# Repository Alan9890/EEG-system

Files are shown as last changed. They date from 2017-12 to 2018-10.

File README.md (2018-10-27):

# EEG-system

NB: If you choose to replicate this project, you do so at your own risk. This is a project that electrically interacts with the human body, and as such there are risks involved. I have designed this system to be as safe as I can make it, but you should still proceed with caution.

This personal project came about as a way to merge two of my interests: physiology and electronics. Electrophysiological signals are the measurable electrical signatures associated with physiological processes. Examples include ECG and EMG for heart and muscle activity respectively. 

## The current state of the project:
Features:
* **Up to 8 channels with 24-bit resolution.** The ADS1298 chip is capable of a maximum of sampling all eight channels at 32k samples/second, but the real limitation is the microcontroller. Practically, a single channel can be broadcast over wifi at about 1000 samples/second. Higher rates can be achieved over a wired connection, or if upgrading the microcontroller.
* **Input referred noise < 5 uV peak-to-peak** (demonstrated to be suitable for EEG, including
SSVEP-based brain-computer interfaces). The system includes up to 12x programmable gain.
* **Battery-powered** for portability, to reduce risk of electric shock, and mitigate contamination from AC noise.
* **Custom GUI** written in Python for device control, data capture, visualization, and analysis
* Capabilities include measuring heart (ECG), muscle (EMG) and brain (EEG) signals.

This repository documents a combination of a python GUI, NodeMCU/arduino code and a PCB design to create a system for acquisition of biological signals. At this point, this project repo includes hardware schematics, circuit board layouts (Eagle CAD files) and firmware (C++), as well as user interface GUI (Python 3.6) which can do the following:
* Connect to a WiFi network and start data collection
* Display real-time readings being collected by the hardware, as well as FFT (frequency spectrum) display.
* Record the time-domain data to a CSV file
* Reset the device
* Toggle the 50 Hz notch filter or high-pass filter on or off
* Change the signal source to choose between the electrodes, the internally generated test signal, or internally shorting the inputs
* Select a different sampling rate, input channel or amplifier gain
* Display the maximum frequency of the signal in the current display window

Below is a photo of the EEG-capturing hardware:

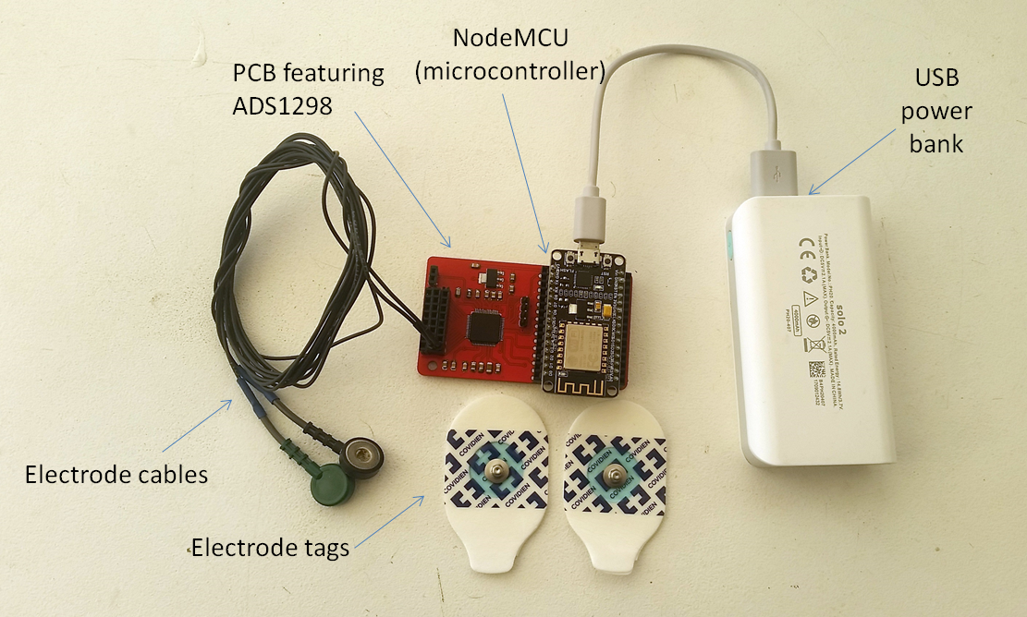
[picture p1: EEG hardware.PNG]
Hardware


Below is a demo of the system capturing alpha waves over my occipital lobe (red text added):

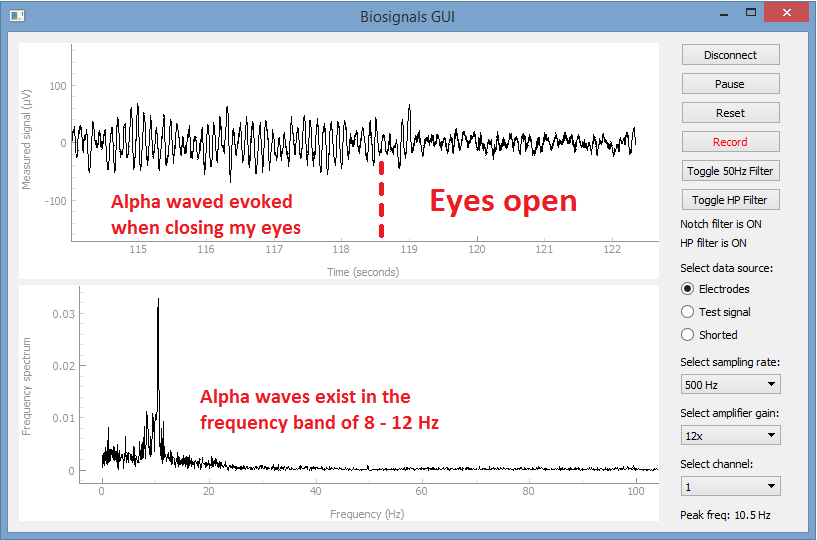
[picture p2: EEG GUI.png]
Example Gui Example GUI


## Areas of ongoing development:
* The wifi transmission of data could do with improvement. It currently employs the UDP "send and forget" protocol, which includes no error checking. This was required to achieve throughput, but might result in interruption of signal during periods of poor signal reception. It might be better to move to bluetooth for transmission.
* Ability to zoom the real-time or FFT plots to a resolution of interest (e.g if working with EMG then we want to see 500Hz - 1000Hz, but for EEG, usually 100Hz is plenty)
* Display multiple channels at once

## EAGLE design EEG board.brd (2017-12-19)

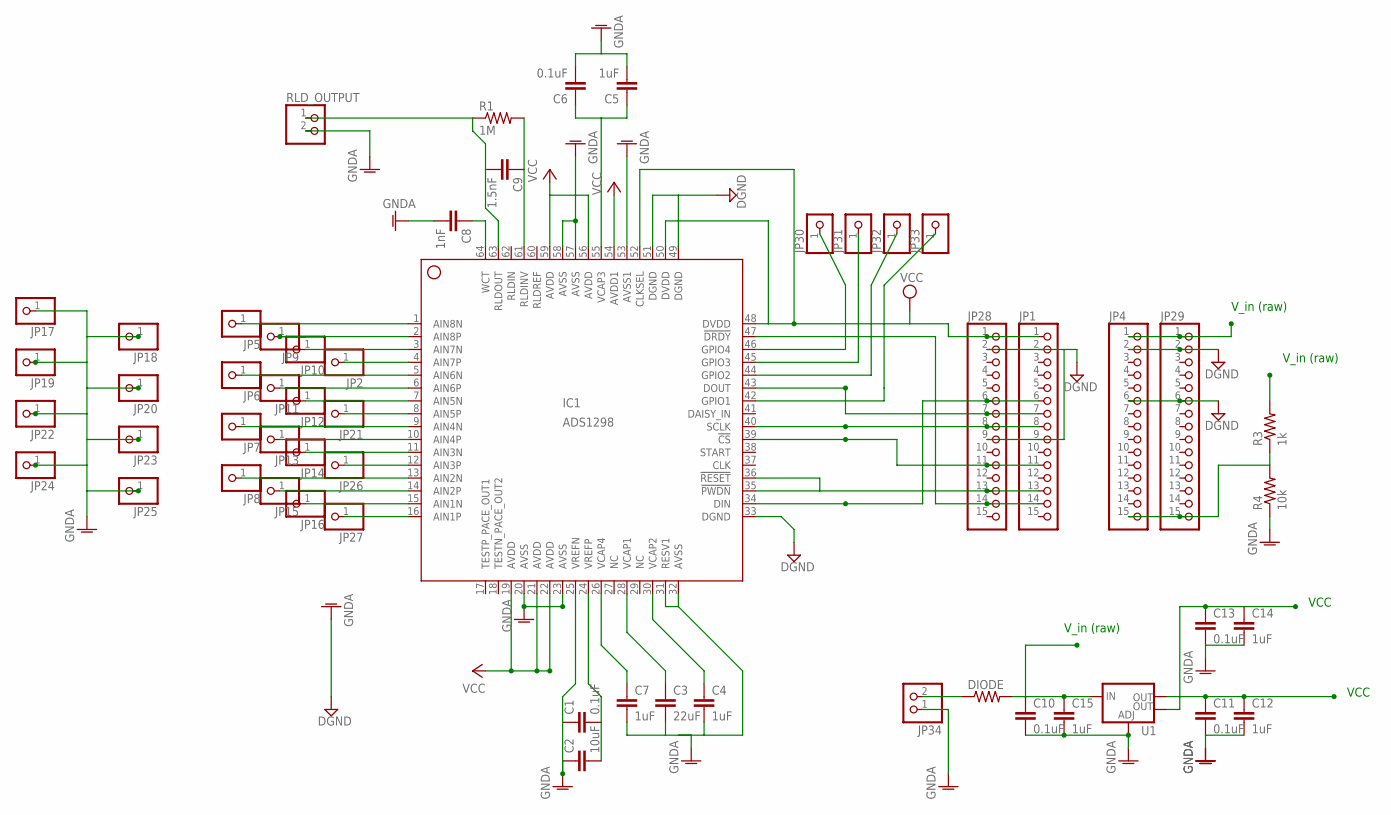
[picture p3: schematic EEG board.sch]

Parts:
C1, C6, C10, C11, C13: 0.1uF; C0805
C2: 10uF; C0805
C3: 22uF; C0805
C4, C5, C7, C12, C14, C15: 1uF; C0805
C8: 1nF; C0805
C9: 1.5nF; C0805
DIODE: R-US_R0805; R0805
IC1: ADS1298; HTQFP-64-PAP
JP1, JP4, JP28, JP29: PINHD-1X15; 1X15
JP2, JP5, JP6, JP7, JP8, JP9, JP10, JP11, JP12, JP13, JP14, JP15, JP16, JP17, JP18, JP19, JP20, JP21, JP22, JP23, JP24, JP25, JP26, JP27, JP30, JP31, JP32, JP33: PINHD-1X1; 1X01
JP34: PINHD-1X2; 1X02
R1: 1M; R0805
R3: 1k; R0805
R4: 10k; R0805
RLD_OUTPUT: PINHD-1X2/90; 1X02/90
U1: V_REG_LM1117SOT223; SOT223

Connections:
9V: DIODE.1, JP34.2
AVDD: C11.1, C12.1, IC1.54 (AVDD1), U1.2 (OUT)
AVDD1: C13.1, C14.1, IC1.19 (AVDD), IC1.21 (AVDD), IC1.22 (AVDD), IC1.56 (AVDD), IC1.59 (AVDD), U1.4 (OUT)
AVSS: C1.1, C2.1, C3.2, C4.2, C5.2, C6.2, C7.2, C8.2, C10.2, C11.2, C12.2, C13.2, C14.2, C15.2, IC1.20 (AVSS), IC1.23 (AVSS), IC1.25 (VREFN), IC1.31 (RESV1), IC1.32 (AVSS), IC1.53 (AVSS1), IC1.57 (AVSS), IC1.58 (AVSS), JP4.2, JP17.1, JP18.1, JP19.1, JP20.1, JP22.1, JP23.1, JP24.1, JP25.1, JP29.2, JP34.1, R4.1, RLD_OUTPUT.2, U1.1 (ADJ)
CS: IC1.39 (!CS), JP1.11, JP28.11
DGND: IC1.33 (DGND), IC1.49 (DGND), IC1.51 (DGND), JP1.2, JP1.9, JP4.6, JP28.2, JP28.9, JP29.6
DIN: IC1.34 (DIN), JP1.6, JP28.6
DOUT: IC1.43 (DOUT), JP1.7, JP28.7
DRDY: IC1.47 (!DRDY), JP1.14, JP28.14
DVDD: IC1.48 (DVDD), IC1.50 (DVDD), IC1.52 (CLKSEL), JP1.1, JP28.1
unnamed: IC1.1 (AIN8N), JP5.1
unnamed: IC1.2 (AIN8P), JP9.1
unnamed: IC1.3 (AIN7N), JP10.1
unnamed: IC1.4 (AIN7P), JP2.1
unnamed: IC1.5 (AIN6N), JP6.1
unnamed: IC1.6 (AIN6P), JP11.1
unnamed: IC1.7 (AIN5N), JP12.1
unnamed: IC1.8 (AIN5P), JP21.1
unnamed: IC1.9 (AIN4N), JP7.1
unnamed: IC1.10 (AIN4P), JP13.1
unnamed: IC1.11 (AIN3N), JP14.1
unnamed: IC1.12 (AIN3P), JP26.1
unnamed: IC1.13 (AIN2N), JP8.1
unnamed: IC1.14 (AIN2P), JP15.1
unnamed: IC1.15 (AIN1N), JP16.1
unnamed: IC1.16 (AIN1P), JP27.1
unnamed: C1.2, C2.2, IC1.24 (VREFP)
unnamed: C3.1, IC1.28 (VCAP1)
unnamed: C4.1, IC1.30 (VCAP2)
unnamed: C5.1, C6.1, IC1.55 (VCAP3)
unnamed: C8.1, IC1.64 (WCT)
unnamed: C7.1, IC1.26 (VCAP4)
unnamed: C9.1, IC1.61 (RLDINV), R1.2
unnamed: JP4.15, JP29.15, R3.1, R4.2
unnamed: C9.2, IC1.63 (RLDOUT), R1.1, RLD_OUTPUT.1
unnamed: IC1.45 (GPIO3), JP31.1
unnamed: IC1.44 (GPIO2), JP32.1
unnamed: IC1.42 (GPIO1), JP33.1
unnamed: IC1.46 (GPIO4), JP30.1
PDWN/RESET: IC1.35 (!PWDN), IC1.36 (!RESET), JP1.13, JP28.13
SCLK: IC1.40 (SCLK), JP1.8, JP28.8
VIN: C10.1, C15.1, DIODE.2, JP4.1, JP29.1, R3.2, U1.3 (IN)

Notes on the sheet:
V_in (raw)
VCC

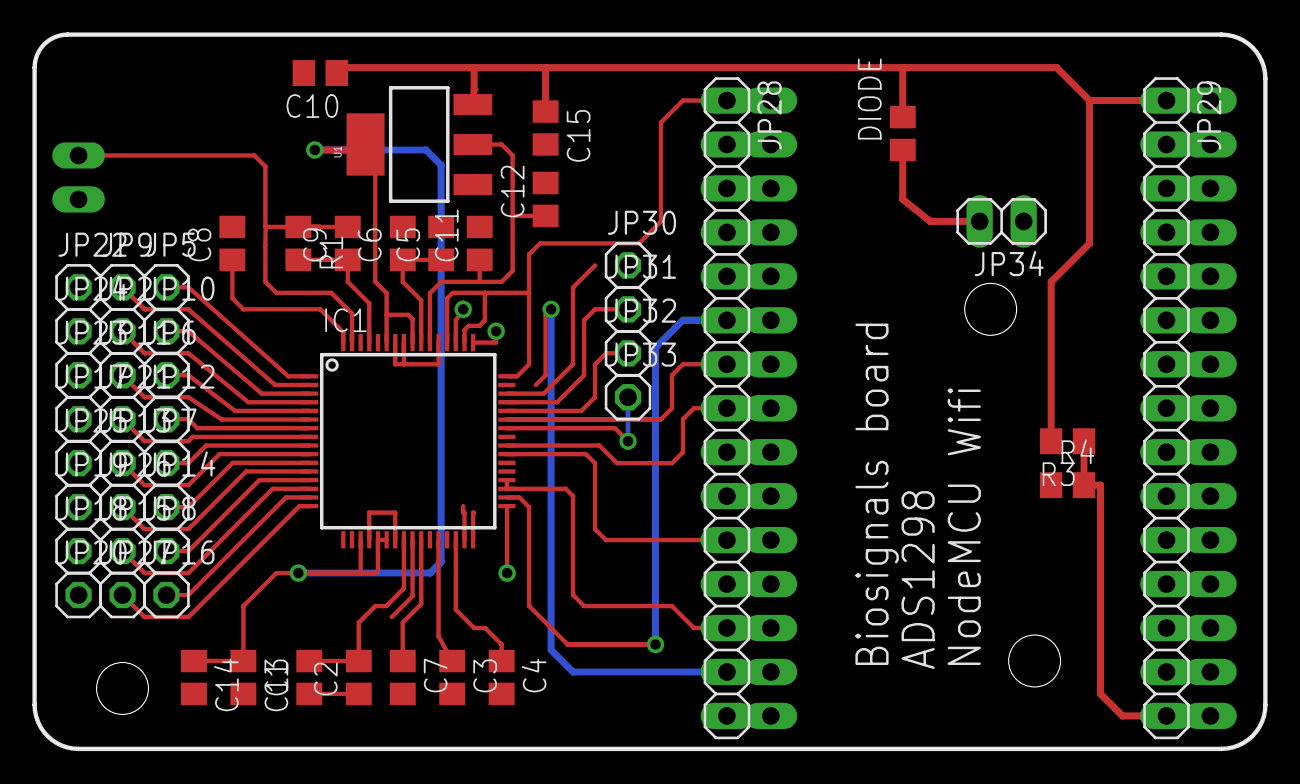
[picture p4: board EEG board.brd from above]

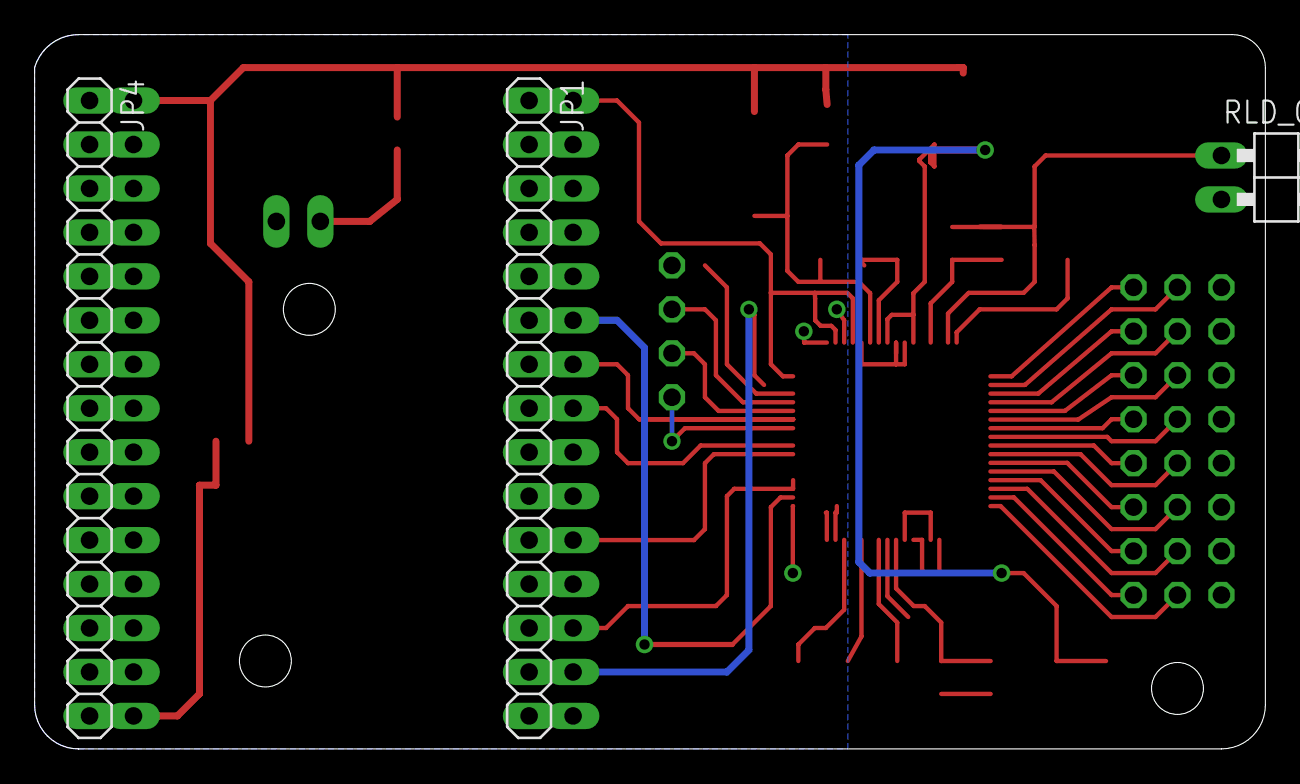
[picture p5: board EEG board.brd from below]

Board: 2 copper layers, 71.1 x 41.3 mm, 55 parts (3 on the bottom side), 42 nets.

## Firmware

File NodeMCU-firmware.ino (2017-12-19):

#include <ESP8266WiFi.h>
#include <WiFiUdp.h>
#include <SPI.h>
#include <Servo.h>

//Default register settings (some can be changed by the GUI):
//==============
//Channel config:
byte CHANNEL_SELECT = 0;
byte GAIN = 0b110;
/* 
Gain bits:
//========
0b000 = 6
0b001 = 1
0b010 = 2
0b011 = 3
0b100 = 4
0b101 = 8
0b110 = 12
 */
 
byte SOURCE = 0b000;
/*
000 = Normal electrode input
001 = Input shorted (for offset or noise measurements)
010 = Used in conjunction with RLD_MEAS bit for RLD measurements. See the Right Leg Drive (RLD) DC Bias Circuit subsection of the ECG-Specific Functions section of the ADS1298 datasheet for more details.
011 = MVDD for supply measurement
100 = Temperature sensor
101 = Test signal
110 = RLD_DRP (positive electrode is the RLD driver)
111 = RLD_DRN (negative electrode is the RLD driver)
*/

//config 1:
#define HR 1 // 0 = low power, 1 = high resolution
#define DAISY_EN 1 // 0 = daisy chain, 1 = multiple feedback
#define CLK_EN 0  //0 = external clock output disabled, 1 = enabled
byte DR = 0b101; 
/*Data rates:
000: HR Mode: 32 kSPS, LP Mode: 16 kSPS
001: HR Mode: 16 kSPS, LP Mode: 8 kSPS
010: HR Mode: 8 kSPS, LP Mode: 4 kSPS
011: HR Mode: 4 kSPS, LP Mode: 2 kSPS
100: HR Mode: 2 kSPS, LP Mode: 1 kSPS
101: HR Mode: 1 kSPS, LP Mode: 500 SPS
110: HR Mode: 500 SPS, LP Mode: 250 SPS
111: Reserved (do not use)
*/

//config 2:
#define WCT_CHOP 0      //variable chopping frequency
#define INT_TEST 1      //internal test signal source
#define TEST_AMP 0      //1mv ref signal
#define TEST_FREQ 0     //pulsed at f_clk/s^21

//config 3:
#define PD_REFBUFF 1    //enabled
#define VREF_4V 0       //use 2.4v reference
#define RLD_MEAS 0      //open
#define RLDREF_INT 1    //internally generated
#define PD_RLD 1        //powered down
#define RLD_LOFF_SENS 0 //enabled
#define RLD_STAT 0      //status bit - read only

//config 4:
#define RESP_FREQ 0b00
#define SINGLE_SHOT 0
#define WCT_TO_RLD 0
#define PD_LOFF_COMP 0 //enable comparator

//LOFF:
#define COMP_TH 0b011   //Comparator threshold
#define VLEAD_OFF_EN 0  //Current source mode
#define ILEAD_OFF 0b11  //Lead-ff detect current: 24nA
#define FLEAD_OFF 0b01  //AC mode

//pin assignments for NodeMCU:
int DRDY = D1;          //ADS1198 data ready, active low
int CS = D4;
int PDWN_RESET = D2;
/*
    MOSI = GPIO13 = D7
    MISO = GPIO12 = D6
    SCLK = GPIO14 = D5
*/

//opcodes:
int WAKEUP = 0x02;
int STANDBY = 0x04;
int RESET = 0x06;
int START = 0x08; 
int STOP = 0x0A;
int RDATAC = 0x10;
int SDATAC = 0x11;
int RDATA = 0x12;

//register map:
int ID = 0x0;
int CONFIG1 = 0x01;
int CONFIG2 = 0x02;
int CONFIG3 = 0x03;
int LOFF = 0x04;
int CHSET[8] = {0x05, 0x06, 0x07, 0x08, 0x09, 0x0A, 0X0B, 0x0C};
int RLD_SENSP = 0x0D;
int RLD_SENSN = 0x0E;
int LOFF_SENSP = 0x0F;
int LOFF_SENSN = 0x10;
int LOFF_FLIP = 0x11;
int LOFF_STATP = 0x12;
int LOFF_STATN = 0x13;
int GPIO = 0x14;
int PACE = 0x15;
int CONFIG4 = 0x17;
int WCT1 = 0x18;
int WCT2 = 0x19;

//wifi variables:
WiFiUDP Udp;
#define localUdpPort 4210  // local port to listen on
char incomingPacket[255];  // buffer for incoming packets

//Variables:
uint8_t  CHH[8], CHM[8], CHL[8]; //recieved A2D bits  
uint32_t STATUS1, Peak_time;
double CHV[8], CHV_S[8], CHV_DC[8], CH_Peak, CH_Threshold = 1; //calculated voltage values

char buffNew[10];
char buff[2048];

uint16_t i;
uint16_t count;
byte sendPacket[1350];

IPAddress remote;
Servo myservo;


void setup() {
myservo.attach(D8);  
ESP8266_config();
ADS1298_config();
WifiConfig();
Serial.println("Waiting for start signal");
}

void loop() {  

  checkUDP();
    
  if (!digitalRead(DRDY)) //if DRDY pulled low
  { 
     
    for (i = 0 ; i < 9 ; i++) 
    {
      //Clock out each byte - 3x status bytes, plus 3x channel 1 bytes
      sendPacket[count] = SPI.transfer(0);
      count++;      
      sendPacket[count] = SPI.transfer(0);
      count++;      
      sendPacket[count] = SPI.transfer(0);
      count++;      
    }

    //send
    if (count >= 1350) //packet size = 9*3*[number of samples for each channel]
    //note: count limit must be a multiple of packet size
    { 
      //broadcast over UDP
      Udp.beginPacket(remote, localUdpPort);
      Udp.write(sendPacket,sizeof(sendPacket));
      Udp.endPacket();

      //clear buffer and count
      count = 0;
    }
    
//    //IF USING SERVO MOTOR DIRECTLY FROM ESP8266:
//    //highpass filter:
//    CHV_DC[CHANNEL_SELECT] = CHV_DC[CHANNEL_SELECT]*0.9 + CHV[CHANNEL_SELECT]*0.1;
//    CHV_S[CHANNEL_SELECT] = CHV[CHANNEL_SELECT] - CHV_DC[CHANNEL_SELECT];
//    
//    //Rectifying and peak detection
//    if (abs(CHV_S[CHANNEL_SELECT]) > CH_Peak) //if new peak is detected
//    {
//      CH_Peak = abs(CHV_S[CHANNEL_SELECT]);   //peak take new value
//      Peak_time = micros();                   //start timing from when peak was detected
//    }
//    else
//      if (micros() - Peak_time > 100)         //if below peak, wait 100ms then slow(ish) decay
//        CH_Peak *= 0.95;
//
//    //Threshold system with hysteresis (AKA schmidt trigger, or double-threshold  to prevent chatter)
//    if (CH_Peak > CH_Threshold) //if thrshold exceeded, activate motor and reduce threshold to 10%
//    {
//      myservo.write(180);
//      CH_Threshold = 0.1;
//    }
//    else        //if lower threshold is not exceeded, move motor back to start and raise threshold again
//    {
//      myservo.write(0);
//      CH_Threshold = 1;
//    }
  }
}

char checkUDP(void)
{
  incomingPacket[0] = 'z';
  int packetSize = Udp.parsePacket();
  if (packetSize)
  {
    // receive incoming UDP packets
    Serial.printf("Received %d bytes from %s, port %d\n", packetSize, remote.toString().c_str(), localUdpPort);
    remote = Udp.remoteIP();
    int len = Udp.read(incomingPacket, UDP_TX_PACKET_MAX_SIZE);
    if (len > 0)
      incomingPacket[len] = 0;

    if (incomingPacket[0] == 'a')
    {
      Serial.println("Start instruction received.");
      SPI.transfer(START); //Activate conversion
      SPI.transfer(RDATAC); //Activate continuous data mode
      Udp.beginPacket(remote, localUdpPort);
      Udp.write('A');
      Udp.endPacket();
    }
    
    if (incomingPacket[0] == 'b')
    {
      Serial.println("Stop instruction received.");
      SPI.transfer(STOP); //Activate conversion
      Udp.beginPacket(remote, localUdpPort);
      Udp.write('B');
      Udp.endPacket();
    }
    
    if (incomingPacket[0] == 'c')
    {
      Serial.println("Reset instruction received.");
      Udp.beginPacket(remote, localUdpPort);
      Udp.write('C');
      Udp.endPacket();

      delay(1000);
      ESP.restart();
    }

    if (incomingPacket[0] == 'd')
    {
      Serial.println("Select electrodes instruction received.");
      SPI.transfer(STOP); //Activate conversion
      delay(5);
      SOURCE = 0b000;
      for (i = 0; i < 8 ; i++)
        WREG(CHSET[i], (GAIN << 4) + SOURCE);
      SPI.transfer(START); //Activate conversion
      Udp.beginPacket(remote, localUdpPort);
      Udp.write('D');
      Udp.endPacket();
    }
    
    if (incomingPacket[0] == 'e')
    {
      Serial.println("Select test signal instruction received.");
      SPI.transfer(STOP); //Activate conversion
      delay(5);
      SOURCE = 0b101;
      for (i = 0; i < 8 ; i++)
        WREG(CHSET[i], (GAIN << 4) + SOURCE);
      SPI.transfer(START); //Activate conversion
      Udp.beginPacket(remote, localUdpPort);
      Udp.write('E');
      Udp.endPacket();
    }

    if (incomingPacket[0] == 'f')
    {
      Serial.println("Select internal short instruction received.");
      SPI.transfer(STOP); //Activate conversion
      delay(5);
      SOURCE = 0b001;
       for (i = 0; i < 8 ; i++)
        WREG(CHSET[i], (GAIN << 4) + SOURCE);
      SPI.transfer(START); //Activate conversion
      Udp.beginPacket(remote, localUdpPort);
      Udp.write('F');
      Udp.endPacket();
    }  

    if (incomingPacket[0] == 'g')
    {
      Serial.println("Select 1x Gain instruction received.");
      SPI.transfer(STOP); //Activate conversion
      delay(5);
      GAIN = 0b001;
      for (i = 0; i < 8 ; i++)
        WREG(CHSET[i], (GAIN << 4) + SOURCE);
      SPI.transfer(START); //Activate conversion
      Udp.beginPacket(remote, localUdpPort);
      Udp.write('G');
      Udp.endPacket();
    }  

    if (incomingPacket[0] == 'h')
    {
      Serial.println("Select 2x Gain instruction received.");
      SPI.transfer(STOP); //Activate conversion
      delay(5);
      GAIN = 0b010;
      for (i = 0; i < 8 ; i++)
        WREG(CHSET[i], (GAIN << 4) + SOURCE);
      SPI.transfer(START); //Activate conversion
      Udp.beginPacket(remote, localUdpPort);
      Udp.write('H');
      Udp.endPacket();
    }  
    
    if (incomingPacket[0] == 'i')
    {
      Serial.println("Select 4x Gain instruction received.");
      SPI.transfer(STOP); //Activate conversion
      delay(5);
      GAIN = 0b100;
      for (i = 0; i < 8 ; i++)
        WREG(CHSET[i], (GAIN << 4) + SOURCE);
      SPI.transfer(START); //Activate conversion
      Udp.beginPacket(remote, localUdpPort);
      Udp.write('I');
      Udp.endPacket();
    }  
    
    if (incomingPacket[0] == 'j')
    {
      Serial.println("Select 6x Gain instruction received.");
      SPI.transfer(STOP); //Activate conversion
      delay(5);
      GAIN = 0b000;
      for (i = 0; i < 8 ; i++)
        WREG(CHSET[i], (GAIN << 4) + SOURCE);
      SPI.transfer(START); //Activate conversion
      Udp.beginPacket(remote, localUdpPort);
      Udp.write('J');
      Udp.endPacket();
    }  
    
    if (incomingPacket[0] == 'k')
    {
      Serial.println("Select 12x Gain instruction received.");
      SPI.transfer(STOP); //Activate conversion
      delay(5);
      GAIN = 0b110;
      for (i = 0; i < 8 ; i++)
        WREG(CHSET[i], (GAIN << 4) + SOURCE);
      SPI.transfer(START); //Activate conversion
      Udp.beginPacket(remote, localUdpPort);
      Udp.write('K');
      Udp.endPacket();
    }  

    if (incomingPacket[0] == 'l')
    {
      Serial.println("Select sampling rate of 500sps instruction received.");
      SPI.transfer(STOP); //Activate conversion
      delay(5);
      DR = 0b110;
      WREG(CONFIG1, (HR<<7) + (DAISY_EN<<6) + (CLK_EN<<5) + DR);
      SPI.transfer(START); //Activate conversion
      Udp.beginPacket(remote, localUdpPort);
      Udp.write('L');
      Udp.endPacket();
    } 

    if (incomingPacket[0] == 'm')
    {
      Serial.println("Select sampling rate of 1000sps instruction received.");
      SPI.transfer(STOP); //Activate conversion
      delay(5);
      DR = 0b101;
      WREG(CONFIG1, (HR<<7) + (DAISY_EN<<6) + (CLK_EN<<5) + DR);
      SPI.transfer(START); //Activate conversion
      Udp.beginPacket(remote, localUdpPort);
      Udp.write('M');
      Udp.endPacket();
    }

    if (incomingPacket[0] == 'n')
    {
      Serial.println("Select sampling rate of 2000sps instruction received.");
      SPI.transfer(STOP); //Activate conversion
      delay(5);
      DR = 0b100;
      WREG(CONFIG1, (HR<<7) + (DAISY_EN<<6) + (CLK_EN<<5) + DR);
      SPI.transfer(START); //Activate conversion
      Udp.beginPacket(remote, localUdpPort);
      Udp.write('N');
      Udp.endPacket();
    }
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

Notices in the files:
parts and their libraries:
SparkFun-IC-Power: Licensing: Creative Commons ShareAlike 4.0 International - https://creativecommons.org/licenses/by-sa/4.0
